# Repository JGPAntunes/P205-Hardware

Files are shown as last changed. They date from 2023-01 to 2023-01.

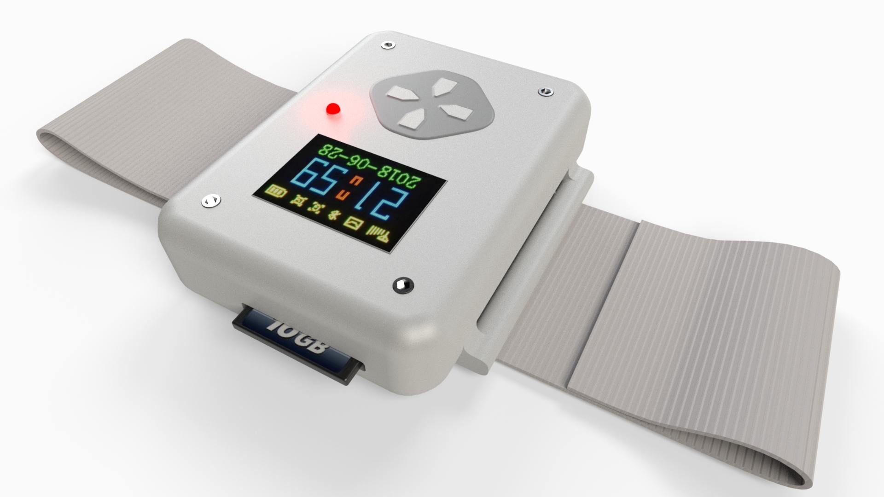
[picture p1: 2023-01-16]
Images/P205_Camera_Camera 2.jpg

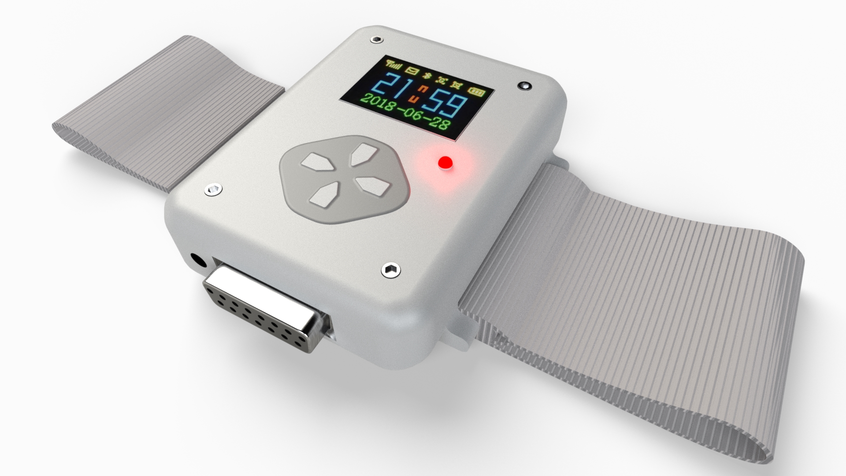
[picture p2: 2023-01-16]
Images/P205_Camera_Camera1.jpg

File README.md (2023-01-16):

# P205-Hardware
This repository was imported from GITLAB manualy, so no commits or branches are available.

This project aims to reliably obtain an ECG and all the signal metrics, and provide real-time alerts. 

These alerts would be sent to the medical staff, and through a graphical interface can confirm the patient ID, contact details and their location (GPS and/or cell triangulation). 

This does not change the fact that it is still a recording device, since the signals are recorded internally on an SD card 
This makes it possible for the data to be interpreted on a hospital environment, by the medical team.

PCB was designed from scratch for this usecase, the Signal Aquisition Medical Board (SAMB).

PCB Specifications:

	• Dual nRF52832 (one for data aquisition and one communications and overhaul system)

	• External RAM for MCU communication bridge

	• ADS1298 and ADS1296 for data aquisition

	• Precision NTC temperature sensing

	• SIM7080G for NB-IoT and GNSS 

	• SD card datalogging

	• BLE comunication (via the master nRF MCU)

	• USB battery charging (type C, no PD charging)

	• Wireless battery charging

	• DSUB-15 connector for eletrodes cable

	• 5mm jack for NTC sensor

	• ESD protection

	• Defibrillator discharge protection

	• OLED display (SPI)

	• Buzzer

	• Small external PCB with UI buttons

PCB Details:

	• Dimentions: 100mm x 95mm.

	• Soldermask: Black.

	• 4 layer IS400 18µm/35µm.

	• Tolerances:

	o OL-TT-TP-PP: 0.100mm (camadas exteriores)

	o OL‐TW: 0.125mm

	o OAR: 0.100mm

	o Via size 0.1mm drill

	o BGA pitch 0.8mm

	• Ni/Au.

	• Double side PCBA.

	• 4 M3 PTH.

	• Star-ground

	• 3 seperated ground planes (analog, digital e power).

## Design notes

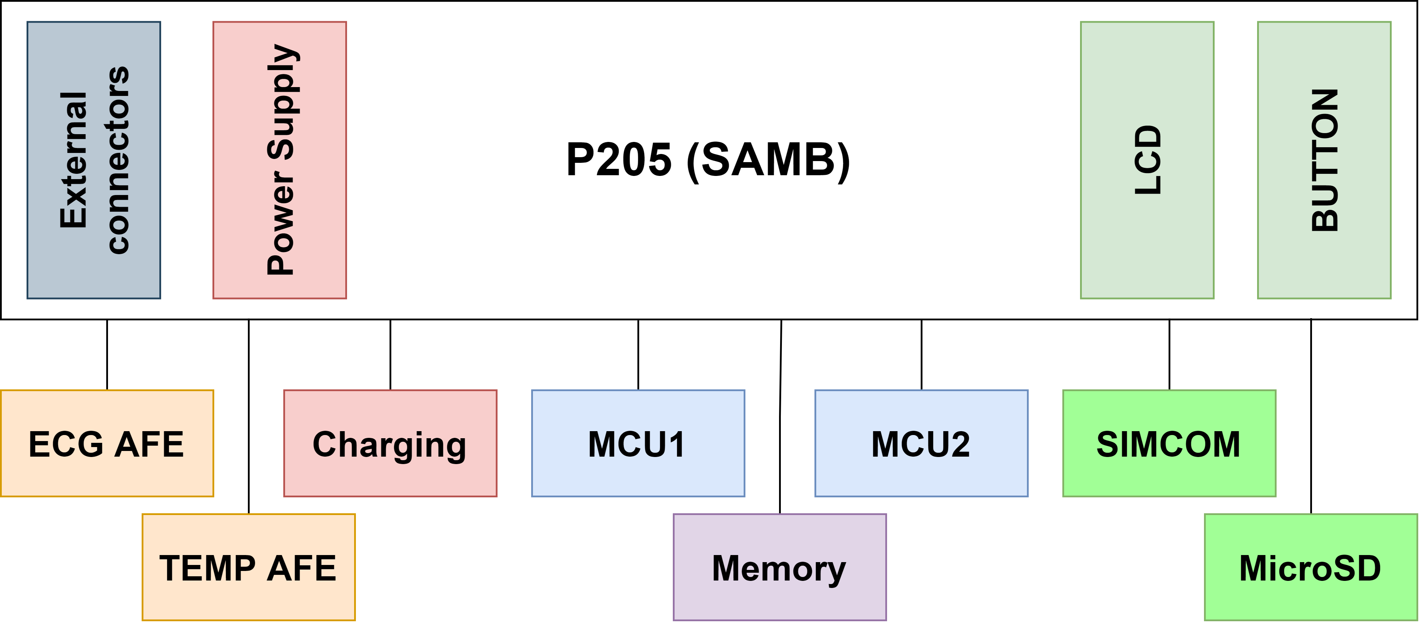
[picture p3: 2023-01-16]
Images/Diagrams/hardware_diagram.png

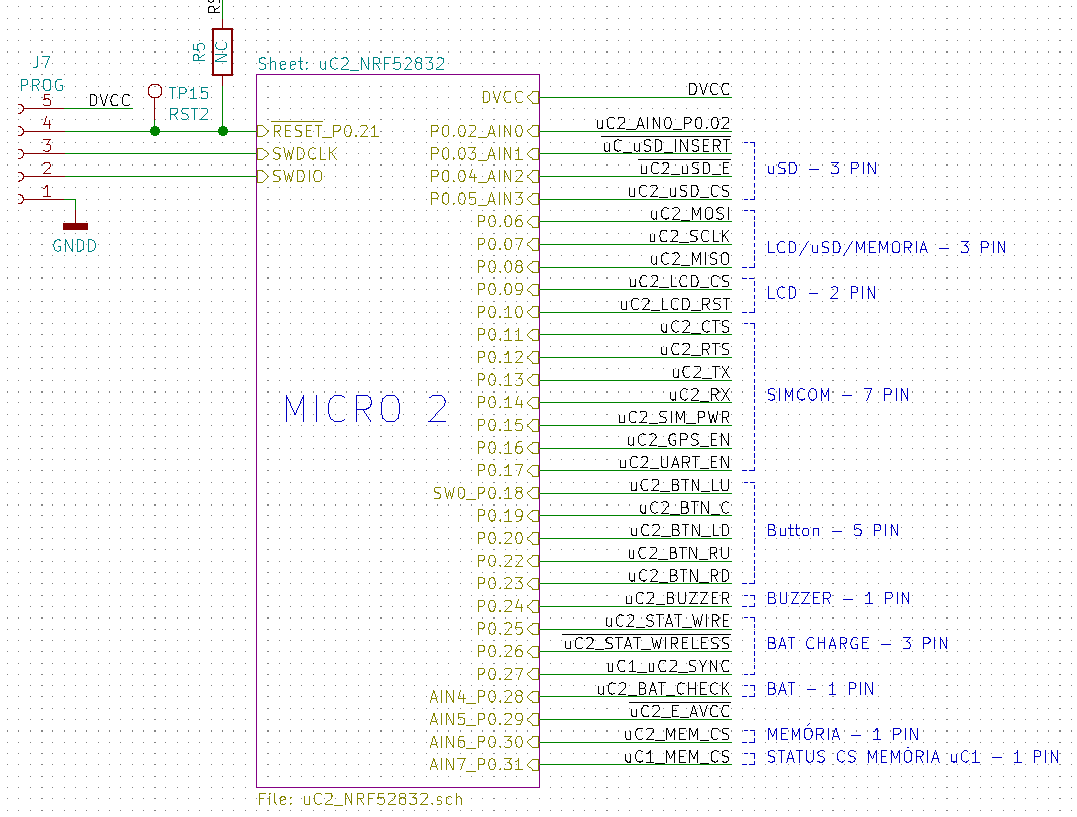
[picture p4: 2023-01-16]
Images/Diagrams/MCU2.png

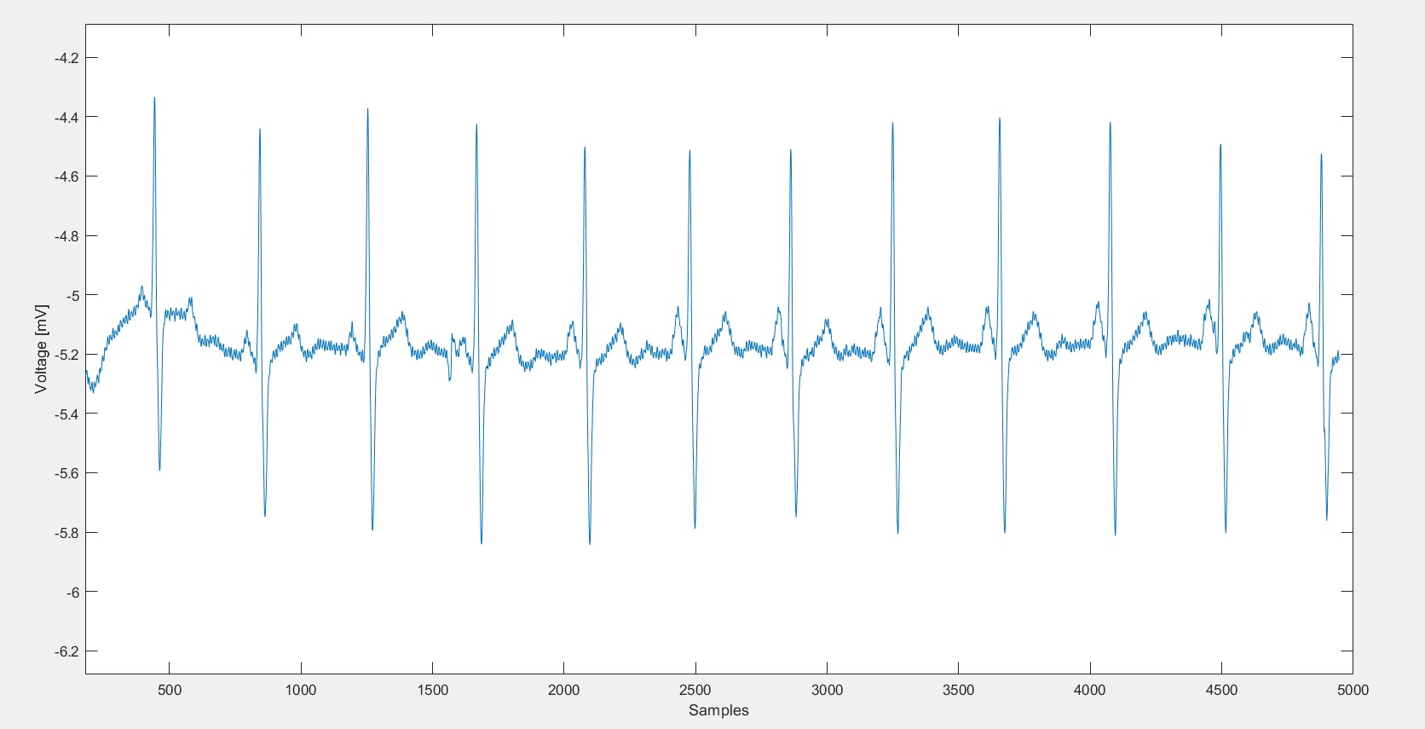
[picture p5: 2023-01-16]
Images/Sensors/filtered33.jpeg

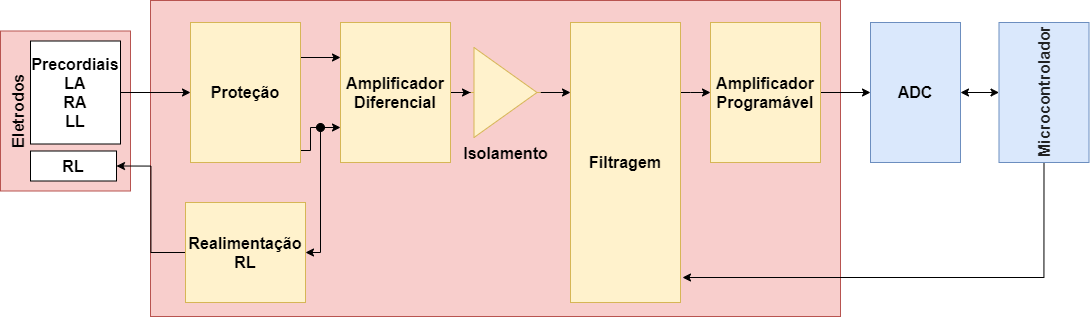
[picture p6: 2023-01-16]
Images/Diagrams/diagramas_sensoresv2.png

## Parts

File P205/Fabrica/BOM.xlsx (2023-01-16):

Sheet: BOM_All
# | References | Manufacturer_Part_Number | Description | Value | Manufacturer_Part_Number | Footprint | Qnt
1 | BZ1 | CSQG703BP | Buzzer, polarized | Buzzer | CSQG703BP | PinHeader_1x02_P1.27mm | 1
2 | C110 | CL05C120JB51PNC | Unpolarized capacitor | 12p | CL05C120JB51PNC | C_0402_1005Metric | 1
3 | C111 | CL05C120JB51PNC | Unpolarized capacitor | 12p | CL05C120JB51PNC | C_0402_1005Metric | 1
4 | C113 | CL05C120JB51PNC | Unpolarized capacitor | 12p | CL05C120JB51PNC | C_0402_1005Metric | 1
5 | C114 | CL05C120JB51PNC | Unpolarized capacitor | 12p | CL05C120JB51PNC | C_0402_1005Metric | 1
6 | C72 | CL05C120JB51PNC | Unpolarized capacitor | 12p | CL05C120JB51PNC | C_0402_1005Metric | 1
7 | C73 | CL05C120JB51PNC | Unpolarized capacitor | 12p | CL05C120JB51PNC | C_0402_1005Metric | 1
8 | C74 | CL05C120JB51PNC | Unpolarized capacitor | 12p | CL05C120JB51PNC | C_0402_1005Metric | 1
9 | C75 | CL05C120JB51PNC | Unpolarized capacitor | 12p | CL05C120JB51PNC | C_0402_1005Metric | 1
10 | C36 | C0402C103K5RAC7411 | Unpolarized capacitor | 22p | C0402C103K5RAC7411 | C_0402_1005Metric | 1
11 | C119 | CL05C221JB51PNC | Unpolarized capacitor | 220p | CL05C221JB51PNC | C_0402_1005Metric | 1
12 | C127 | CL05C221JB51PNC | Unpolarized capacitor | 220p | CL05C221JB51PNC | C_0402_1005Metric | 1
13 | C128 | CL05C221JB51PNC | Unpolarized capacitor | 220p | CL05C221JB51PNC | C_0402_1005Metric | 1
14 | C15 | CL05C221JB51PNC | Unpolarized capacitor | 220p | CL05C221JB51PNC | C_0402_1005Metric | 1
15 | C16 | CL05C221JB51PNC | Unpolarized capacitor | 220p | CL05C221JB51PNC | C_0402_1005Metric | 1
16 | C80 | CL05C221JB51PNC | Unpolarized capacitor | 220p | CL05C221JB51PNC | C_0402_1005Metric | 1
17 | C19 | 04025C102KAT4A | Unpolarized capacitor | 1n | 04025C102KAT4A | C_0402_1005Metric | 1
18 | C20 | 04025C102KAT4A | Unpolarized capacitor | 1n | 04025C102KAT4A | C_0402_1005Metric | 1
19 | C125 | C0402C103K5RAC7411 | Unpolarized capacitor | 10n | C0402C103K5RAC7411 | C_0402_1005Metric | 1
20 | C126 | C0402C103K5RAC7411 | Unpolarized capacitor | 10n | C0402C103K5RAC7411 | C_0402_1005Metric | 1
21 | C17 | C0402C103K5RAC7411 | Unpolarized capacitor | 10n | C0402C103K5RAC7411 | C_0402_1005Metric | 1
22 | C18 | C0402C103K5RAC7411 | Unpolarized capacitor | 10n | C0402C103K5RAC7411 | C_0402_1005Metric | 1
23 | C27 | C0402C103K5RAC7411 | Unpolarized capacitor | 10n | C0402C103K5RAC7411 | C_0402_1005Metric | 1
24 | C42 | C0402C103K5RAC7411 | Unpolarized capacitor | 10n | C0402C103K5RAC7411 | C_0402_1005Metric | 1
25 | C45 | C0402C103K5RAC7411 | Unpolarized capacitor | 10n | C0402C103K5RAC7411 | C_0402_1005Metric | 1
26 | C91 | C0402C103K5RAC7411 | Unpolarized capacitor | 10n | C0402C103K5RAC7411 | C_0402_1005Metric | 1
27 | C92 | C0402C103K5RAC7411 | Unpolarized capacitor | 10n | C0402C103K5RAC7411 | C_0402_1005Metric | 1
28 | C94 | C0402C103K5RAC7411 | Unpolarized capacitor | 10n | C0402C103K5RAC7411 | C_0402_1005Metric | 1
29 | C95 | C0402C103K5RAC7411 | Unpolarized capacitor | 10n | C0402C103K5RAC7411 | C_0402_1005Metric | 1
30 | C_TUNE2_1 | C0402C103K5RAC7411 | Unpolarized capacitor | 10n | C0402C103K5RAC7411 | C_0402_1005Metric | 1
31 | C_TUNE2_2 | C0402C103K5RAC7411 | Unpolarized capacitor | 10n | C0402C103K5RAC7411 | C_0402_1005Metric | 1
32 | C_TUNE2_3 | C0402C103K5RAC7411 | Unpolarized capacitor | 10n | C0402C103K5RAC7411 | C_0402_1005Metric | 1
33 | C1 | GCM155R71H104KE02D | Unpolarized capacitor | 100n | GCM155R71H104KE02D | C_0402_1005Metric | 1
34 | C101 | GCM155R71H104KE02D | Unpolarized capacitor | 100n | GCM155R71H104KE02D | C_0402_1005Metric | 1
35 | C103 | GCM155R71H104KE02D | Unpolarized capacitor | 100n | GCM155R71H104KE02D | C_0402_1005Metric | 1
36 | C105 | GCM155R71H104KE02D | Unpolarized capacitor | 100n | GCM155R71H104KE02D | C_0402_1005Metric | 1
37 | C116 | GCM155R71H104KE02D | Unpolarized capacitor | 100n | GCM155R71H104KE02D | C_0402_1005Metric | 1
38 | C117 | GCM155R71H104KE02D | Unpolarized capacitor | 100n | GCM155R71H104KE02D | C_0402_1005Metric | 1
39 | C121 | GCM155R71H104KE02D | Unpolarized capacitor | 100n | GCM155R71H104KE02D | C_0402_1005Metric | 1
40 | C124 | GCM155R71H104KE02D | Unpolarized capacitor | 100n | GCM155R71H104KE02D | C_0402_1005Metric | 1
41 | C23 | GCM155R71H104KE02D | Unpolarized capacitor | 100n | GCM155R71H104KE02D | C_0402_1005Metric | 1
42 | C24 | GCM155R71H104KE02D | Unpolarized capacitor | 100n | GCM155R71H104KE02D | C_0402_1005Metric | 1
43 | C30 | GCM155R71H104KE02D | Unpolarized capacitor | 100n | GCM155R71H104KE02D | C_0402_1005Metric | 1
44 | C31 | GCM155R71H104KE02D | Unpolarized capacitor | 100n | GCM155R71H104KE02D | C_0402_1005Metric | 1
45 | C32 | GCM155R71H104KE02D | Unpolarized capacitor | 100n | GCM155R71H104KE02D | C_0402_1005Metric | 1
46 | C4 | GCM155R71H104KE02D | Unpolarized capacitor | 100n | GCM155R71H104KE02D | C_0402_1005Metric | 1
47 | C40 | GCM155R71H104KE02D | Unpolarized capacitor | 100n | GCM155R71H104KE02D | C_0402_1005Metric | 1
48 | C41 | GCM155R71H104KE02D | Unpolarized capacitor | 100n | GCM155R71H104KE02D | C_0402_1005Metric | 1
49 | C43 | GCM155R71H104KE02D | Unpolarized capacitor | 100n | GCM155R71H104KE02D | C_0402_1005Metric | 1
50 | C44 | GCM155R71H104KE02D | Unpolarized capacitor | 100n | GCM155R71H104KE02D | C_0402_1005Metric | 1
51 | C48 | GCM155R71H104KE02D | Unpolarized capacitor | 100n | GCM155R71H104KE02D | C_0402_1005Metric | 1
52 | C49 | GCM155R71H104KE02D | Unpolarized capacitor | 100n | GCM155R71H104KE02D | C_0402_1005Metric | 1
53 | C5 | GCM155R71H104KE02D | Unpolarized capacitor | 100n | GCM155R71H104KE02D | C_0402_1005Metric | 1
54 | C50 | GCM155R71H104KE02D | Unpolarized capacitor | 100n | GCM155R71H104KE02D | C_0402_1005Metric | 1
55 | C51 | GCM155R71H104KE02D | Unpolarized capacitor | 100n | GCM155R71H104KE02D | C_0402_1005Metric | 1
56 | C52 | GCM155R71H104KE02D | Unpolarized capacitor | 100n | GCM155R71H104KE02D | C_0402_1005Metric | 1
57 | C58 | GCM155R71H104KE02D | Unpolarized capacitor | 100n | GCM155R71H104KE02D | C_0402_1005Metric | 1
58 | C59 | GCM155R71H104KE02D | Unpolarized capacitor | 100n | GCM155R71H104KE02D | C_0402_1005Metric | 1
59 | C60 | GCM155R71H104KE02D | Unpolarized capacitor | 100n | GCM155R71H104KE02D | C_0402_1005Metric | 1
60 | C64 | GCM155R71H104KE02D | Unpolarized capacitor | 100n | GCM155R71H104KE02D | C_0402_1005Metric | 1
61 | C67 | GCM155R71H104KE02D | Unpolarized capacitor | 100n | GCM155R71H104KE02D | C_0402_1005Metric | 1
62 | C68 | GCM155R71H104KE02D | Unpolarized capacitor | 100n | GCM155R71H104KE02D | C_0402_1005Metric | 1
63 | C71 | GCM155R71H104KE02D | Unpolarized capacitor | 100n | GCM155R71H104KE02D | C_0402_1005Metric | 1
64 | C77 | GCM155R71H104KE02D | Unpolarized capacitor | 100n | GCM155R71H104KE02D | C_0402_1005Metric | 1
65 | C78 | GCM155R71H104KE02D | Unpolarized capacitor | 100n | GCM155R71H104KE02D | C_0402_1005Metric | 1
66 | C82 | GCM155R71H104KE02D | Unpolarized capacitor | 100n | GCM155R71H104KE02D | C_0402_1005Metric | 1
67 | C84 | GCM155R71H104KE02D | Unpolarized capacitor | 100n | GCM155R71H104KE02D | C_0402_1005Metric | 1
68 | C89 | C1005X5R1E474K050BB | Unpolarized capacitor | 0.47u | C1005X5R1E474K050BB | C_0402_1005Metric | 1
69 | C90 | C1005X5R1E474K050BB | Unpolarized capacitor | 0.47u | C1005X5R1E474K050BB | C_0402_1005Metric | 1
70 | C_TUNE1_3 | C1005X5R1E474K050BB | Unpolarized capacitor | 0.47u | C1005X5R1E474K050BB | C_0402_1005Metric | 1
71 | C100 | GRT155R61E105KE01D | Unpolarized capacitor | 1u | GRT155R61E105KE01D | C_0402_1005Metric | 1
72 | C102 | GRT155R61E105KE01D | Unpolarized capacitor | 1u | GRT155R61E105KE01D | C_0402_1005Metric | 1
73 | C118 | GRT155R61E105KE01D | Unpolarized capacitor | 1u | GRT155R61E105KE01D | C_0402_1005Metric | 1
74 | C129 | GRT155R61E105KE01D | Unpolarized capacitor | 1u | GRT155R61E105KE01D | C_0402_1005Metric | 1
75 | C130 | GRT155R61E105KE01D | Unpolarized capacitor | 1u | GRT155R61E105KE01D | C_0402_1005Metric | 1
76 | C25 | GRT155R61E105KE01D | Unpolarized capacitor | 1u | GRT155R61E105KE01D | C_0402_1005Metric | 1
77 | C26 | GRT155R61E105KE01D | Unpolarized capacitor | 1u | GRT155R61E105KE01D | C_0402_1005Metric | 1
78 | C28 | GRT155R61E105KE01D | Unpolarized capacitor | 1u | GRT155R61E105KE01D | C_0402_1005Metric | 1
79 | C29 | GRT155R61E105KE01D | Unpolarized capacitor | 1u | GRT155R61E105KE01D | C_0402_1005Metric | 1
80 | C33 | GRT155R61E105KE01D | Unpolarized capacitor | 1u | GRT155R61E105KE01D | C_0402_1005Metric | 1
81 | C34 | GRT155R61E105KE01D | Unpolarized capacitor | 1u | GRT155R61E105KE01D | C_0402_1005Metric | 1
82 | C46 | GRT155R61E105KE01D | Unpolarized capacitor | 1u | GRT155R61E105KE01D | C_0402_1005Metric | 1
83 | C47 | GRT155R61E105KE01D | Unpolarized capacitor | 1u | GRT155R61E105KE01D | C_0402_1005Metric | 1
84 | C54 | GRT155R61E105KE01D | Unpolarized capacitor | 1u | GRT155R61E105KE01D | C_0402_1005Metric | 1
85 | C55 | GRT155R61E105KE01D | Unpolarized capacitor | 1u | GRT155R61E105KE01D | C_0402_1005Metric | 1
86 | C56 | GRT155R61E105KE01D | Unpolarized capacitor | 1u | GRT155R61E105KE01D | C_0402_1005Metric | 1
87 | C62 | GRT155R61E105KE01D | Unpolarized capacitor | 1u | GRT155R61E105KE01D | C_0402_1005Metric | 1
88 | C79 | GRT155R61E105KE01D | Unpolarized capacitor | 1u | GRT155R61E105KE01D | C_0402_1005Metric | 1
89 | C83 | GRT155R61E105KE01D | Unpolarized capacitor | 1u | GRT155R61E105KE01D | C_0402_1005Metric | 1
90 | C93 | GRT155R61E105KE01D | Unpolarized capacitor | 1u | GRT155R61E105KE01D | C_0402_1005Metric | 1
91 | C96 | GRT155R61E105KE01D | Unpolarized capacitor | 1u | GRT155R61E105KE01D | C_0402_1005Metric | 1
92 | C_TUNE1_1 | GRT155R61E105KE01D | Unpolarized capacitor | 1u | GRT155R61E105KE01D | C_0402_1005Metric | 1
93 | C_TUNE1_2 | GRT155R61E105KE01D | Unpolarized capacitor | 1u | GRT155R61E105KE01D | C_0402_1005Metric | 1
94 | C115 | CL21A475KLCLQNC | Unpolarized capacitor | 4.7u | CL21A475KLCLQNC | C_0805_2012Metric | 1
95 | C123 | CL21A475KLCLQNC | Unpolarized capacitor | 4.7u | CL21A475KLCLQNC | C_0805_2012Metric | 1
96 | C76 | CL21A475KLCLQNC | Unpolarized capacitor | 4.7u | CL21A475KLCLQNC | C_0805_2012Metric | 1
97 | C106 | TMK212BBJ106MG-T | Unpolarized capacitor | 10u | TMK212BBJ106MG-T | C_0805_2012Metric | 1
98 | C131 | TMK212BBJ106MG-T | Unpolarized capacitor | 10u | TMK212BBJ106MG-T | C_0805_2012Metric | 1
99 | C21 | TMK212BBJ106MG-T | Unpolarized capacitor | 10u | TMK212BBJ106MG-T | C_0805_2012Metric | 1
100 | C22 | TMK212BBJ106MG-T | Unpolarized capacitor | 10u | TMK212BBJ106MG-T | C_0805_2012Metric | 1
101 | C35 | TMK212BBJ106MG-T | Unpolarized capacitor | 10u | TMK212BBJ106MG-T | C_0805_2012Metric | 1
102 | C37 | TMK212BBJ106MG-T | Unpolarized capacitor | 10u | TMK212BBJ106MG-T | C_0805_2012Metric | 1
103 | C38 | TMK212BBJ106MG-T | Unpolarized capacitor | 10u | TMK212BBJ106MG-T | C_0805_2012Metric | 1
104 | C39 | TMK212BBJ106MG-T | Unpolarized capacitor | 10u | TMK212BBJ106MG-T | C_0805_2012Metric | 1
105 | C53 | TMK212BBJ106MG-T | Unpolarized capacitor | 10u | TMK212BBJ106MG-T | C_0805_2012Metric | 1
106 | C57 | TMK212BBJ106MG-T | Unpolarized capacitor | 10u | TMK212BBJ106MG-T | C_0805_2012Metric | 1
107 | C69 | TMK212BBJ106MG-T | Unpolarized capacitor | 10u | TMK212BBJ106MG-T | C_0805_2012Metric | 1
108 | C70 | TMK212BBJ106MG-T | Unpolarized capacitor | 10u | TMK212BBJ106MG-T | C_0805_2012Metric | 1
109 | C97 | TMK212BBJ106MG-T | Unpolarized capacitor | 10u | TMK212BBJ106MG-T | C_0805_2012Metric | 1
110 | C98 | TMK212BBJ106MG-T | Unpolarized capacitor | 10u | TMK212BBJ106MG-T | C_0805_2012Metric | 1
111 | C99 | TMK212BBJ106MG-T | Unpolarized capacitor | 10u | TMK212BBJ106MG-T | C_0805_2012Metric | 1
112 | C85 | TAJB107K006TNJ | Polarized capacitor, US symbol | 100u | TAJB107K006TNJ | C_1210_3225Metric | 1
113 | C86 | TAJB107K006TNJ | Polarized capacitor, US symbol | 100u | TAJB107K006TNJ | C_1210_3225Metric | 1
114 | C87 | TAJB107K006TNJ | Polarized capacitor, US symbol | 100u | TAJB107K006TNJ | C_1210_3225Metric | 1
115 | C10 |  | Unpolarized capacitor | NC |  |  | 1
116 | C104 |  | Unpolarized capacitor | NC |  |  | 1
117 | C107 |  | Unpolarized capacitor | NC |  |  | 1
118 | C108 |  | Unpolarized capacitor | NC |  |  | 1
119 | C109 |  | Unpolarized capacitor | NC |  |  | 1
120 | C11 |  | Unpolarized capacitor | NC |  |  | 1
121 | C112 |  | Unpolarized capacitor | NC |  |  | 1
122 | C12 |  | Unpolarized capacitor | NC |  |  | 1
123 | C120 |  | Unpolarized capacitor | NC |  |  | 1
124 | C122 |  | Unpolarized capacitor | NC |  |  | 1
125 | C13 |  | Unpolarized capacitor | NC |  |  | 1
126 | C14 |  | Unpolarized capacitor | NC |  |  | 1
127 | C6 |  | Unpolarized capacitor | NC |  |  | 1
128 | C7 |  | Unpolarized capacitor | NC |  |  | 1
129 | C8 |  | Unpolarized capacitor | NC |  |  | 1
130 | C81 |  | Unpolarized capacitor | NC |  |  | 1
131 | C9 |  | Unpolarized capacitor | NC |  |  | 1
132 | C2 |  | Unpolarized capacitor | TUNE |  | C_0402_1005Metric | 1
133 | C3 |  | Unpolarized capacitor | TUNE |  | C_0402_1005Metric | 1
134 | C88 |  | Unpolarized capacitor | TUNE |  | C_0402_1005Metric | 1
135 | D32 | APHBM2012LVBDZGKC | Dual LED, cathodes on pins 2 and 4 | APHBM2012LVBDZGKC | APHBM2012LVBDZGKC | LED_2C | 1
136 | D1 | DESD5V0U1BA-7 | Bidirectional transient-voltage-suppression diode | DESD5V0U1BA-7 | DESD5V0U1BA-7 | D_SOD-323 | 1
137 | D10 | DESD5V0U1BA-7 | Bidirectional transient-voltage-suppression diode | DESD5V0U1BA-7 | DESD5V0U1BA-7 | D_SOD-323 | 1
138 | D11 | DESD5V0U1BA-7 | Bidirectional transient-voltage-suppression diode | DESD5V0U1BA-7 | DESD5V0U1BA-7 | D_SOD-323 | 1
139 | D12 | DESD5V0U1BA-7 | Bidirectional transient-voltage-suppression diode | DESD5V0U1BA-7 | DESD5V0U1BA-7 | D_SOD-323 | 1
140 | D13 | DESD5V0U1BA-7 | Bidirectional transient-voltage-suppression diode | DESD5V0U1BA-7 | DESD5V0U1BA-7 | D_SOD-323 | 1
141 | D16 | DESD5V0U1BA-7 | Bidirectional transient-voltage-suppression diode | DESD5V0U1BA-7 | DESD5V0U1BA-7 | D_SOD-323 | 1
142 | D17 | DESD5V0U1BA-7 | Bidirectional transient-voltage-suppression diode | DESD5V0U1BA-7 | DESD5V0U1BA-7 | D_SOD-323 | 1
143 | D18 | DESD5V0U1BA-7 | Bidirectional transient-voltage-suppression diode | DESD5V0U1BA-7 | DESD5V0U1BA-7 | D_SOD-323 | 1
144 | D19 | DESD5V0U1BA-7 | Bidirectional transient-voltage-suppression diode | DESD5V0U1BA-7 | DESD5V0U1BA-7 | D_SOD-323 | 1
145 | D2 | DESD5V0U1BA-7 | Bidirectional transient-voltage-suppression diode | DESD5V0U1BA-7 | DESD5V0U1BA-7 | D_SOD-323 | 1
146 | D20 | DESD5V0U1BA-7 | Bidirectional transient-voltage-suppression diode | DESD5V0U1BA-7 | DESD5V0U1BA-7 | D_SOD-323 | 1
147 | D21 | DESD5V0U1BA-7 | Bidirectional transient-voltage-suppression diode | DESD5V0U1BA-7 | DESD5V0U1BA-7 | D_SOD-323 | 1
148 | D22 | DESD5V0U1BA-7 | Bidirectional transient-voltage-suppression diode | DESD5V0U1BA-7 | DESD5V0U1BA-7 | D_SOD-323 | 1
149 | D23 | DESD5V0U1BA-7 | Bidirectional transient-voltage-suppression diode | DESD5V0U1BA-7 | DESD5V0U1BA-7 | D_SOD-323 | 1
150 | D24 | DESD5V0U1BA-7 | Bidirectional transient-voltage-suppression diode | DESD5V0U1BA-7 | DESD5V0U1BA-7 | D_SOD-323 | 1
151 | D25 | DESD5V0U1BA-7 | Bidirectional transient-voltage-suppression diode | DESD5V0U1BA-7 | DESD5V0U1BA-7 | D_SOD-323 | 1
152 | D26 | DESD5V0U1BA-7 | Bidirectional transient-voltage-suppression diode | DESD5V0U1BA-7 | DESD5V0U1BA-7 | D_SOD-323 | 1
153 | D27 | DESD5V0U1BA-7 | Bidirectional transient-voltage-suppression diode | DESD5V0U1BA-7 | DESD5V0U1BA-7 | D_SOD-323 | 1
154 | D28 | DESD5V0U1BA-7 | Bidirectional transient-voltage-suppression diode | DESD5V0U1BA-7 | DESD5V0U1BA-7 | D_SOD-323 | 1
155 | D29 | DESD5V0U1BA-7 | Bidirectional transient-voltage-suppression diode | DESD5V0U1BA-7 | DESD5V0U1BA-7 | D_SOD-323 | 1
156 | D3 | DESD5V0U1BA-7 | Bidirectional transient-voltage-suppression diode | DESD5V0U1BA-7 | DESD5V0U1BA-7 | D_SOD-323 | 1
157 | D4 | DESD5V0U1BA-7 | Bidirectional transient-voltage-suppression diode | DESD5V0U1BA-7 | DESD5V0U1BA-7 | D_SOD-323 | 1
158 | D5 | DESD5V0U1BA-7 | Bidirectional transient-voltage-suppression diode | DESD5V0U1BA-7 | DESD5V0U1BA-7 | D_SOD-323 | 1
159 | D6 | DESD5V0U1BA-7 | Bidirectional transient-voltage-suppression diode | DESD5V0U1BA-7 | DESD5V0U1BA-7 | D_SOD-323 | 1
160 | D7 | DESD5V0U1BA-7 | Bidirectional transient-voltage-suppression diode | DESD5V0U1BA-7 | DESD5V0U1BA-7 | D_SOD-323 | 1
161 | D8 | DESD5V0U1BA-7 | Bidirectional transient-voltage-suppression diode | DESD5V0U1BA-7 | DESD5V0U1BA-7 | D_SOD-323 | 1
162 | D9 | DESD5V0U1BA-7 | Bidirectional transient-voltage-suppression diode | DESD5V0U1BA-7 | DESD5V0U1BA-7 | D_SOD-323 | 1
163 | D14 | FML340A-W | Schottky diode | FML340A-W | FML340A-W | D_SMA | 1
164 | D15 | FML340A-W | Schottky diode | FML340A-W | FML340A-W | D_SMA | 1
165 | D30 | FML340A-W | Schottky diode | FML340A-W | FML340A-W | D_SMA | 1
166 | D31 | FML340A-W | Schottky diode | FML340A-W | FML340A-W | D_SMA | 1
167 | D33 | FML340A-W | Schottky diode | FML340A-W | FML340A-W | D_SMA | 1
168 | D34 | FML340A-W | Schottky diode | FML340A-W | FML340A-W | D_SMA | 1
169 | FB1 | BLM21SP601SH1D | Ferrite bead | BLM21SP601SH1D | BLM21SP601SH1D | R_0805_2012Metric | 1
170 | FB2 | BLM21SP601SH1D | Ferrite bead | BLM21SP601SH1D | BLM21SP601SH1D | R_0805_2012Metric | 1
171 | IC6 | 23K640-I/ST | Microchip Technology SRAM, 23K640-I/ST- 64kbit | 23K640-I_ST | 23K640-I/ST | SOP65P640X120-8N | 1
172 | IC1 | ADS1296RIZXGT | 6-Channel, 24-Bit Analog-To-Digital Converter w/Integrated Respiration | ADS1296RIZXGT | ADS1296RIZXGT | BGA64C80P8X8_800X800X145 | 1
173 | IC2 | ADS1298IPAG | 8-Channel 24-bit ADC With Integrated ECG Front End | ADS1298IPAG | ADS1298IPAG | QFP50P1200X1200X120-64N | 1
174 | IC3 | BQ51050BRHLR | Qi (WPC) Compliant Highly Integrated Secondary-Side Direct Lithium Ion Charger. | BQ51050BRHLR | BQ51050BRHLR | BQ51050BRHLR | 1
175 | IC4 | SN74HCS00QPWRQ1 | Logic Gates | SN74HCS00QPWRQ1 | SN74HCS00QPWRQ1 | SOP65P640X120-14N | 1
176 | J14 | 12401598E4#2A |  | 12401598E4#2A | 12401598E4#2A | AMPHENOL_12401598E4#2A | 1
177 | J3 | WS |  | 70-IWAS4532AGB140KF1 | WS | PinSocket_1x02_P2.54mm_Vertical | 1
178 | J2 | M40-4010446 |  | Batt | M40-4010446 | M404010446 | 1
179 | J8 | WS | Generic connector, single row, 01x14, | EXP1 | WS | PinSocket_2x08_P1.27mm_Horizontal | 1
180 | J16 | WS | Generic connector, single row, 01x14, | EXP2 | WS | PinSocket_2x08_P1.27mm_Horizontal | 1
181 | J1 | MEM2061-01-188-00-A | MEM2061 Series 8 Position 1.1 mm Pitch Push-Push MicroSD SMT Memory Card Connector | MEM2061-01-188-00-A | MEM2061-01-188-00-A | MEM20610118800A | 1
182 | J5 | WS | Audio Jack, 2 Poles (Mono / TS), Grounded Sleeve, Switched T Pole (Normalling) | NTC Connector | WS | M404010246 | 1
183 | J6 | WS | Generic connector, single row, 01x05 | PROG | WS | PinSocket_1x05_P2.54mm_Vertical | 1
184 | J7 | WS | Generic connector, single row, 01x05 | PROG | WS | PinSocket_1x05_P2.54mm_Vertical | 1
185 | J10 | SIM8051-6-0-14-00-A | SIM Card | SIM_Card | SIM8051-6-0-14-00-A | SIM8051601401A | 1
186 | J12 | U.FL-R-SMT-1(10) |  | U.FL-R-SMT-1(10) | U.FL-R-SMT-1(10) | CONUFL001-SMD | 1
187 | J13 | U.FL-R-SMT-1(10) |  | U.FL-R-SMT-1(10) | U.FL-R-SMT-1(10) | CONUFL001-SMD | 1
188 | J15 | U.FL-R-SMT-1(10) |  | U.FL-R-SMT-1(10) | U.FL-R-SMT-1(10) | CONUFL001-SMD | 1
189 | J11 | WS | Generic connector, double row, 02x03 | USB/BATT | WS | PinHeader_2x03_P2.54mm_Vertical | 1
190 | J17 | WS | Generic connector, double row, 02x03 | USB/BATT | WS | PinHeader_2x03_P2.54mm_Vertical | 1
191 | L2 | 7447840115 | Inductor | 15n | 7447840115 | L_0402_1005Metric | 1
192 | L8 | 7447840115 | Inductor | 15n | 7447840115 | L_0402_1005Metric | 1
193 | L6 | TYA2520121R0M-10 | Inductor | 1uH | TYA2520121R0M-10 | L_1008_2520Metric | 1
194 | L1 | MLZ1608M100WTD25 | Inductor | 10u | MLZ1608M100WTD25 | L_0603_1608Metric | 1
195 | L9 | MLZ1608M100WTD25 | Inductor | 10u | MLZ1608M100WTD25 | L_0603_1608Metric | 1
196 | L7 |  | Inductor symbol for simulation only | NC |  |  | 1
197 | L3 |  | Inductor | TUNE |  | C_0402_1005Metric | 1
198 | L4 |  | Inductor | TUNE |  | C_0402_1005Metric | 1
199 | L5 |  | Inductor | TUNE |  | C_0402_1005Metric | 1
200 | NT1 |  | Net tie, 3 pins, tee | STAR GROUND |  | NINJA_STAR_GROUND | 1
201 | Q1 | DMG2305UX-7 | MOSFET P-Ch 20V 5A Enhancement SOT23 Diodes | DMG2305 | DMG2305UX-7 | SOT-23 | 1
202 | Q3 | DMG2305UX-7 | MOSFET P-Ch 20V 5A Enhancement SOT23 Diodes | DMG2305 | DMG2305UX-7 | SOT-23 | 1
203 | Q4 | DMG2305UX-7 | MOSFET P-Ch 20V 5A Enhancement SOT23 Diodes | DMG2305 | DMG2305UX-7 | SOT-23 | 1
204 | Q2 | PMV15ENEAR | N-MOSFET transistor, gate/source/drain | PMV15ENEAR | PMV15ENEAR | SOT-23 | 1
205 | R36 | SFR01MZPJ000 | Resistor | 0 | SFR01MZPJ000 | R_0402_1005Metric | 1
206 | R39 | SFR01MZPJ000 | Resistor | 0 | SFR01MZPJ000 | R_0402_1005Metric | 1
207 | R42 | SFR01MZPJ000 | Resistor | 0 | SFR01MZPJ000 | R_0402_1005Metric | 1
208 | R43 | SFR01MZPJ000 | Resistor | 0 | SFR01MZPJ000 | R_0402_1005Metric | 1
209 | R53 | SFR01MZPJ000 | Resistor | 0 | SFR01MZPJ000 | R_0402_1005Metric | 1
210 | R54 | SFR01MZPJ000 | Resistor | 0 | SFR01MZPJ000 | R_0402_1005Metric | 1
211 | R55 | SFR01MZPJ000 | Resistor | 0 | SFR01MZPJ000 | R_0402_1005Metric | 1
212 | R56 | SFR01MZPJ000 | Resistor | 0 | SFR01MZPJ000 | R_0402_1005Metric | 1
213 | R88 | CRCW06030000Z0EAC | Resistor | 0 | CRCW06030000Z0EAC | R_0603_1608Metric | 1
214 | R63 | CRCW0402330RJNEDHP | Resistor | 200 | CRCW0402330RJNEDHP | R_0402_1005Metric | 1
215 | R77 | Resistor_SMD:R_0402_1005Metric | Resistor | 200 | Resistor_SMD:R_0402_1005Metric | R_0402_1005Metric | 1
216 | R75 | CRCW0402270RFKEDHP | Resistor | 270 | CRCW0402270RFKEDHP | R_0402_1005Metric | 1
217 | R103 | CRCW0402330RJNEDHP | Resistor | 330 | CRCW0402330RJNEDHP | R_0402_1005Metric | 1
218 | R104 | CRCW0402330RJNEDHP | Resistor | 330 | CRCW0402330RJNEDHP | R_0402_1005Metric | 1
219 | R44 | CRCW0402330RJNEDHP | Resistor | 330 | CRCW0402330RJNEDHP | R_0402_1005Metric | 1
220 | R45 | CRCW0402330RJNEDHP | Resistor | 330 | CRCW0402330RJNEDHP | R_0402_1005Metric | 1
221 | R64 | CRCW0402330RJNEDHP | Resistor | 330 | CRCW0402330RJNEDHP | R_0402_1005Metric | 1
222 | R65 | CRCW0402330RJNEDHP | Resistor | 330 | CRCW0402330RJNEDHP | R_0402_1005Metric | 1
223 | R68 | CRCW0402330RJNEDHP | Resistor | 330 | CRCW0402330RJNEDHP | R_0402_1005Metric | 1
224 | R86 | CRCW0402330RJNEDHP | Resistor | 330 | CRCW0402330RJNEDHP | R_0402_1005Metric | 1
225 | R57 | RG1005N-3161-W-T1 | Resistor | 3.24k | RG1005N-3161-W-T1 | R_0402_1005Metric | 1
226 | R1 | SG73P1ETTP512J | Resistor | 5.1k | SG73P1ETTP512J | R_0402_1005Metric | 1
227 | R10 | SG73P1ETTP512J | Resistor | 5.1k | SG73P1ETTP512J | R_0402_1005Metric | 1
228 | R11 | SG73P1ETTP512J | Resistor | 5.1k | SG73P1ETTP512J | R_0402_1005Metric | 1
229 | R12 | SG73P1ETTP512J | Resistor | 5.1k | SG73P1ETTP512J | R_0402_1005Metric | 1
230 | R13 | SG73P1ETTP512J | Resistor | 5.1k | SG73P1ETTP512J | R_0402_1005Metric | 1
231 | R2 | SG73P1ETTP512J | Resistor | 5.1k | SG73P1ETTP512J | R_0402_1005Metric | 1
232 | R37 | SG73P1ETTP512J | Resistor | 5.1k | SG73P1ETTP512J | R_0402_1005Metric | 1
233 | R38 | SG73P1ETTP512J | Resistor | 5.1k | SG73P1ETTP512J | R_0402_1005Metric | 1
234 | R40 | SG73P1ETTP512J | Resistor | 5.1k | SG73P1ETTP512J | R_0402_1005Metric | 1
235 | R58 | SG73P1ETTP512J | Resistor | 5.1k | SG73P1ETTP512J | R_0402_1005Metric | 1
236 | R74 | SG73P1ETTP512J | Resistor | 5.1k | SG73P1ETTP512J | R_0402_1005Metric | 1
237 | R101 | RC0402JR-7W10KL | Resistor | 10k | RC0402JR-7W10KL | R_0402_1005Metric | 1
238 | R102 | RC0402JR-7W10KL | Resistor | 10k | RC0402JR-7W10KL | R_0402_1005Metric | 1
239 | R105 | RC0402JR-7W10KL | Resistor | 10k | RC0402JR-7W10KL | R_0402_1005Metric | 1
240 | R24 | MOS3CT631R103J | Resistor | 10k | MOS3CT631R103J | R_Axial_DIN0617_L17.0mm_D6.0mm | 1
241 | R25 | MOS3CT631R103J | Resistor | 10k | MOS3CT631R103J | R_Axial_DIN0617_L17.0mm_D6.0mm | 1
242 | R31 | RC0402JR-7W10KL | Resistor | 10k | RC0402JR-7W10KL | R_0402_1005Metric | 1
243 | R32 | RC0402JR-7W10KL | Resistor | 10k | RC0402JR-7W10KL | R_0402_1005Metric | 1
244 | R34 | RC0402JR-7W10KL | Resistor | 10k | RC0402JR-7W10KL | R_0402_1005Metric | 1
245 | R41 | RC0402JR-7W10KL | Resistor | 10k | RC0402JR-7W10KL | R_0402_1005Metric | 1
246 | R59 | RC0402JR-7W10KL | Resistor | 10k | RC0402JR-7W10KL | R_0402_1005Metric | 1
247 | R60 | RC0402JR-7W10KL | Resistor | 10k | RC0402JR-7W10KL | R_0402_1005Metric | 1
248 | R61 | CRCW0402100KFKEDC | Resistor | 10k | CRCW0402100KFKEDC | R_0402_1005Metric | 1
249 | R62 | CRCW0402100KFKEDC | Resistor | 10k | CRCW0402100KFKEDC | R_0402_1005Metric | 1
250 | R72 | RC0402JR-7W10KL | Resistor | 10k | RC0402JR-7W10KL | R_0402_1005Metric | 1
251 | R78 | RC0402JR-7W10KL | Resistor | 10k | RC0402JR-7W10KL | R_0402_1005Metric | 1
252 | R80 | RC0402JR-7W10KL | Resistor | 10k | RC0402JR-7W10KL | R_0402_1005Metric | 1
253 | R82 | RC0402JR-7W10KL | Resistor | 10k | RC0402JR-7W10KL | R_0402_1005Metric | 1
254 | R97 | RC0402JR-7W10KL | Resistor | 10k | RC0402JR-7W10KL | R_0402_1005Metric | 1
255 | R98 | RC0402JR-7W10KL | Resistor | 10k | RC0402JR-7W10KL | R_0402_1005Metric | 1
256 | R76 | ERJ-2RKF4222X | Resistor | 42.2k | ERJ-2RKF4222X | R_0402_1005Metric | 1
257 | R3 | 667-ERJ-2RKF7152X | Resistor | 71.5k | 667-ERJ-2RKF7152X | R_0402_1005Metric | 1
258 | R48 | 667-ERJ-2RKF7152X | Resistor | 71.5k | 667-ERJ-2RKF7152X | R_0402_1005Metric | 1
259 | R100 | CRCW0402100KFKEDC | Resistor | 100k | CRCW0402100KFKEDC | R_0402_1005Metric | 1
260 | R14 | RSF3WSJT-73-100K | Resistor | 100k | RSF3WSJT-73-100K | R_Axial_DIN0516_L15.5mm_D5.0mm | 1
261 | R15 | RSF3WSJT-73-100K | Resistor | 100k | RSF3WSJT-73-100K | R_Axial_DIN0516_L15.5mm_D5.0mm | 1
262 | R16 | RSF3WSJT-73-100K | Resistor | 100k | RSF3WSJT-73-100K | R_Axial_DIN0516_L15.5mm_D5.0mm | 1
263 | R17 | RSF3WSJT-73-100K | Resistor | 100k | RSF3WSJT-73-100K | R_Axial_DIN0516_L15.5mm_D5.0mm | 1
264 | R18 | RSF3WSJT-73-100K | Resistor | 100k | RSF3WSJT-73-100K | R_Axial_DIN0516_L15.5mm_D5.0mm | 1
265 | R19 | RSF3WSJT-73-100K | Resistor | 100k | RSF3WSJT-73-100K | R_Axial_DIN0516_L15.5mm_D5.0mm | 1
266 | R20 | RSF3WSJT-73-100K | Resistor | 100k | RSF3WSJT-73-100K | R_Axial_DIN0516_L15.5mm_D5.0mm | 1
267 | R21 | RSF3WSJT-73-100K | Resistor | 100k | RSF3WSJT-73-100K | R_Axial_DIN0516_L15.5mm_D5.0mm | 1
268 | R22 | RSF3WSJT-73-100K | Resistor | 100k | RSF3WSJT-73-100K | R_Axial_DIN0516_L15.5mm_D5.0mm | 1
269 | R23 | RSF3WSJT-73-100K | Resistor | 100k | RSF3WSJT-73-100K | R_Axial_DIN0516_L15.5mm_D5.0mm | 1
270 | R4 | CRCW0402100KFKEDC | Resistor | 100k | CRCW0402100KFKEDC | R_0402_1005Metric | 1
271 | R26 | RCS04021M00FKED | Resistor | 1M | RCS04021M00FKED | R_0402_1005Metric | 1
272 | R27 | RCS04021M00FKED | Resistor | 1M | RCS04021M00FKED | R_0402_1005Metric | 1
273 | R28 | RCS04021M00FKED | Resistor | 1M | RCS04021M00FKED | R_0402_1005Metric | 1
274 | R29 | RCS04021M00FKED | Resistor | 1M | RCS04021M00FKED | R_0402_1005Metric | 1
275 | R30 | RCS04021M00FKED | Resistor | 1M | RCS04021M00FKED | R_0402_1005Metric | 1
276 | R33 | RCS04021M00FKED | Resistor | 1M | RCS04021M00FKED | R_0402_1005Metric | 1
277 | R35 | RCS04021M00FKED | Resistor | 1M | RCS04021M00FKED | R_0402_1005Metric | 1
278 | R46 | RCS04021M00FKED | Resistor | 1M | RCS04021M00FKED | R_0402_1005Metric | 1
279 | R47 | RCS04021M00FKED | Resistor | 1M | RCS04021M00FKED | R_0402_1005Metric | 1
280 | R6 | RCS04021M00FKED | Resistor | 1M | RCS04021M00FKED | R_0402_1005Metric | 1
281 | R7 | RCS04021M00FKED | Resistor | 1M | RCS04021M00FKED | R_0402_1005Metric | 1
282 | R8 | RCS04021M00FKED | Resistor | 1M | RCS04021M00FKED | R_0402_1005Metric | 1
283 | R9 | RCS04021M00FKED | Resistor | 1M | RCS04021M00FKED | R_0402_1005Metric | 1
284 | R51 | CRCW04021M13FKED | Resistor | 1.13M | CRCW04021M13FKED | R_0402_1005Metric | 1
285 | R52 | CRCW04021M18FKED | Resistor | 1.18M | CRCW04021M18FKED | R_0402_1005Metric | 1
286 | R49 | RC0402JR-071M2L | Resistor | 1.2M | RC0402JR-071M2L | R_0402_1005Metric | 1
287 | R50 | CRCW04021M60FKEDC | Resistor | 1.6M | CRCW04021M60FKEDC | R_0402_1005Metric | 1
288 | R5 |  | Resistor | NC |  |  | 1
289 | R66 |  | Resistor | NC |  |  | 1
290 | R67 |  | Resistor | NC |  |  | 1
291 | R69 |  | Resistor | NC |  |  | 1
292 | R70 |  | Resistor | NC |  |  | 1
293 | R71 |  | Resistor | NC |  |  | 1
294 | R83 |  | Resistor | NC |  |  | 1
295 | R87 |  | Resistor | NC |  |  | 1
296 | R89 |  | Resistor | NC |  |  | 1
297 | R90 |  | Resistor | NC |  |  | 1
298 | R91 |  | Resistor | NC |  |  | 1
299 | RN1 | CAT16-2701F4LF | 4 resistor network, parallel topology, SIP package | CAT16-2701F4LF | CAT16-2701F4LF | R_Cat16-4 | 1
300 | S1 | SKRHACE010 |  | SKRHACE010 | SKRHACE010 | SKRHAAE010 | 1
301 | U5 | ADS1114IDGSR | ADC | ADS1114IDGSR | ADS1114IDGSR | SOP50P490X110-10N | 1
302 | U15 | B39162B9415K610 | B39162B9415K610 | B39162B9415K610 | B39162B9415K610 | B39162B9415K610 | 1
303 | U14 | BGU8009,115 | BGU8009 | BGU8009,115 | BGU8009,115 | BGU8009,115 | 1
304 | U3 | LP3874EMPX-3.3/NOPB |  | LP3874EMP-3.3_NOPB | LP3874EMPX-3.3/NOPB | SOT-223-5 | 1
305 | U6 | MAX6070AAUT30+T |  | MAX6070AAUT30+T | MAX6070AAUT30+T | SOT-23-6 | 1
306 | U2 | MCP1501T-33E/CHY |  | MCP1501T-33E_CHY | MCP1501T-33E/CHY | SOT-23-6 | 1
307 | U13 | NXB0108BQ-Q100X |  | NXB0108 | NXB0108BQ-Q100X | WQFN-20-1EP_2.5x4.5mm_P0.5mm_EP1x2.9mm | 1
308 | U9 |  |  | OLED_2.49" |  |  | 1
309 | U17 | PI5C3257ZHDEX |  | PI5C3257 | PI5C3257ZHDEX | QFN-16-1EP_3x3mm_P0.5mm_EP1.7x1.7mm | 1
310 | U18 | PI5C3257ZHDEX |  | PI5C3257 | PI5C3257ZHDEX | QFN-16-1EP_3x3mm_P0.5mm_EP1.7x1.7mm | 1
311 | U8 | S2-108HB-Z308J |  | SIM7080G | S2-108HB-Z308J | XCVR_SIM7080G | 1
312 | U12 | SN74HCS02QPWRQ1 | Logic Gates | SN74HCS02-Q1 | SN74HCS02QPWRQ1 | TSSOP-14_4.4x5mm_P0.65mm | 1
313 | U4 | TLV3202AID | Dual operational amplifier | TLV3202AID | TLV3202AID | SOIC-8_3.9x4.9mm_P1.27mm | 1
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

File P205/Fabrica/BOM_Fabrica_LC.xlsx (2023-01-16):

# | References | Manufacturer_Part_Number | Description | Value | Footprint | Qnt
1 | C110 | CL05C120JB51PNC | Unpolarized capacitor | 12p | C_0402_1005Metric | 8
2 | C119 | CL05C221JB51PNC | Unpolarized capacitor | 220p | C_0402_1005Metric | 6
3 | C125 | C0402C103K5RAC7411 | Unpolarized capacitor | 10n | C_0402_1005Metric | 14
4 | C1 | GCM155R71H104KE02D | Unpolarized capacitor | 100n | C_0402_1005Metric | 35
5 | C89 | C1005X5R1E474K050BB | Unpolarized capacitor | 0.47u | C_0402_1005Metric | 3
6 | C100 | GRT155R61E105KE01D | Unpolarized capacitor | 1u | C_0402_1005Metric | 23
7 | C106 | TMK212BBJ106MG-T | Unpolarized capacitor | 10u | C_0805_2012Metric | 15
8 | D1 | DESD5V0U1BA-7 | Bidirectional transient-voltage-suppression diode | DESD5V0U1BA-7 | D_SOD-323 | 27
9 | D14 | FML340A-W | Schottky diode | FML340A-W | D_SMA | 6
10 | IC6 | 23K640-I/ST | Microchip Technology SRAM, 23K640-I/ST- 64kbit | 23K640-I_ST | SOP65P640X120-8N | 1
11 | IC1 | ADS1296RIZXGT | 6-Channel, 24-Bit Analog-To-Digital Converter w/Integrated Respiration | ADS1296RIZXGT | BGA64C80P8X8_800X800X145 | 1
12 | IC2 | ADS1298IPAG | 8-Channel 24-bit ADC With Integrated ECG Front End | ADS1298IPAG | QFP50P1200X1200X120-64N | 1
13 | IC3 | BQ51050BRHLR | Qi (WPC) Compliant Highly Integrated Secondary-Side Direct Lithium Ion Charger. | BQ51050BRHLR | BQ51050BRHLR | 1
14 | IC4 | SN74HCS00QPWRQ1 | Logic Gates | SN74HCS00QPWRQ1 | SOP65P640X120-14N | 1
15 | J14 | 12401598E4#2A |  | USB-C | AMPHENOL_12401598E4#2A | 1
16 | J2 | M40-4010446 |  | Batt | M404010446 | 1
17 | J1 | MEM2061-01-188-00-A | MEM2061 Series 8 Position 1.1 mm Pitch Push-Push MicroSD SMT Memory Card Connector | MEM2061-01-188-00-A | MEM20610118800A | 1
18 | J10 | SIM8051-6-0-14-00-A | SIM Card | SIM_Card | SIM8051601401A | 1
19 | J12 | U.FL-R-SMT-1(10) |  | U.FL-R-SMT-1(10) | CONUFL001-SMD | 3
20 | L2 | 7447840115 | Inductor | 15n | L_0402_1005Metric | 2
21 | Q1 | DMG2305UX-7 | MOSFET P-Ch 20V 5A Enhancement SOT23 Diodes | DMG2305 | SOT-23 | 4
22 | R36 | SFR01MZPJ000 | Resistor | 0 | R_0402_1005Metric | 9
23 | R103 | CRCW0402330RJNEDHP | Resistor | 330 | R_0402_1005Metric | 8
24 | R1 | SG73P1ETTP512J | Resistor | 5.1k | R_0402_1005Metric | 11
25 | R101 | RC0402JR-7W10KL | Resistor | 10k | R_0402_1005Metric | 17
26 | R26 | RCS04021M00FKED | Resistor | 1M | R_0402_1005Metric | 13
27 | U5 | ADS1114IDGSR | ADC | ADS1114IDGSR | SOP50P490X110-10N | 1
28 | U15 | B39162B9415K610 | B39162B9415K610 | B39162B9415K610 | B39162B9415K610 | 1
29 | U14 | BGU8009,115 | BGU8009 | BGU8009,115 | BGU8009,115 | 1
30 | U13 | NXB0108BQ-Q100X |  | NXB0108 | WQFN-20-1EP_2.5x4.5mm_P0.5mm_EP1x2.9mm | 1
31 | U17 | PI5C3257ZHDEX |  | PI5C3257 | QFN-16-1EP_3x3mm_P0.5mm_EP1.7x1.7mm | 2
32 | U8 | S2-108HB-Z308J |  | SIM7080G | XCVR_SIM7080G | 1
33 | U12 | SN74HCS02QPWRQ1 | Logic Gates | SN74HCS02-Q1 | TSSOP-14_4.4x5mm_P0.65mm | 1
34 | U1 | TLV9062QDGKRQ1 | Dual operational amplifier | TLV9062QDGKRQ1 | VSSOP-8_3.0x3.0mm_P0.65mm | 1
35 | U7 | nRF52832-QFAB-R |  | nRF52832 | QFN-48-1EP_6x6mm_P0.4mm_EP4.6x4.6mm | 2
36 | X1 | ECS-.327-12.5-12R-TR | Crystals 32.768kHz 12.5pF -40C +85C | ECS-.327-12.5-12R-TR | ECS32712512RTR | 2
37 | X3 | ECS-.327-12.5-12R-TR | Crystals 32.768kHz 12.5pF -40C +85C | ECS-.327-12.5-12R-TR | ECS32712512RTR | 1
38 | X2 | ECS-320-8-37B-7KM-TR | Crystals 32MHz 8pf 50 ohms -20C to 70C 7ppm | ECS-320-8-37B-7KM-TR | ECS320837B7KMTR | 1
39 | Y1 | SR4G008 | Antennas 1559-1609MHz Avg. Eff >75% Linear | SR4G008 | SR4G008 | 1
40 | Z1 | BQ25300RTER | Battery Management Standalone 1-cell, 17-V, 3.0-A battery charger 16-WQFN | BQ25300RTER | QFN50P300X300X80-17N-D | 1
Total: | 230

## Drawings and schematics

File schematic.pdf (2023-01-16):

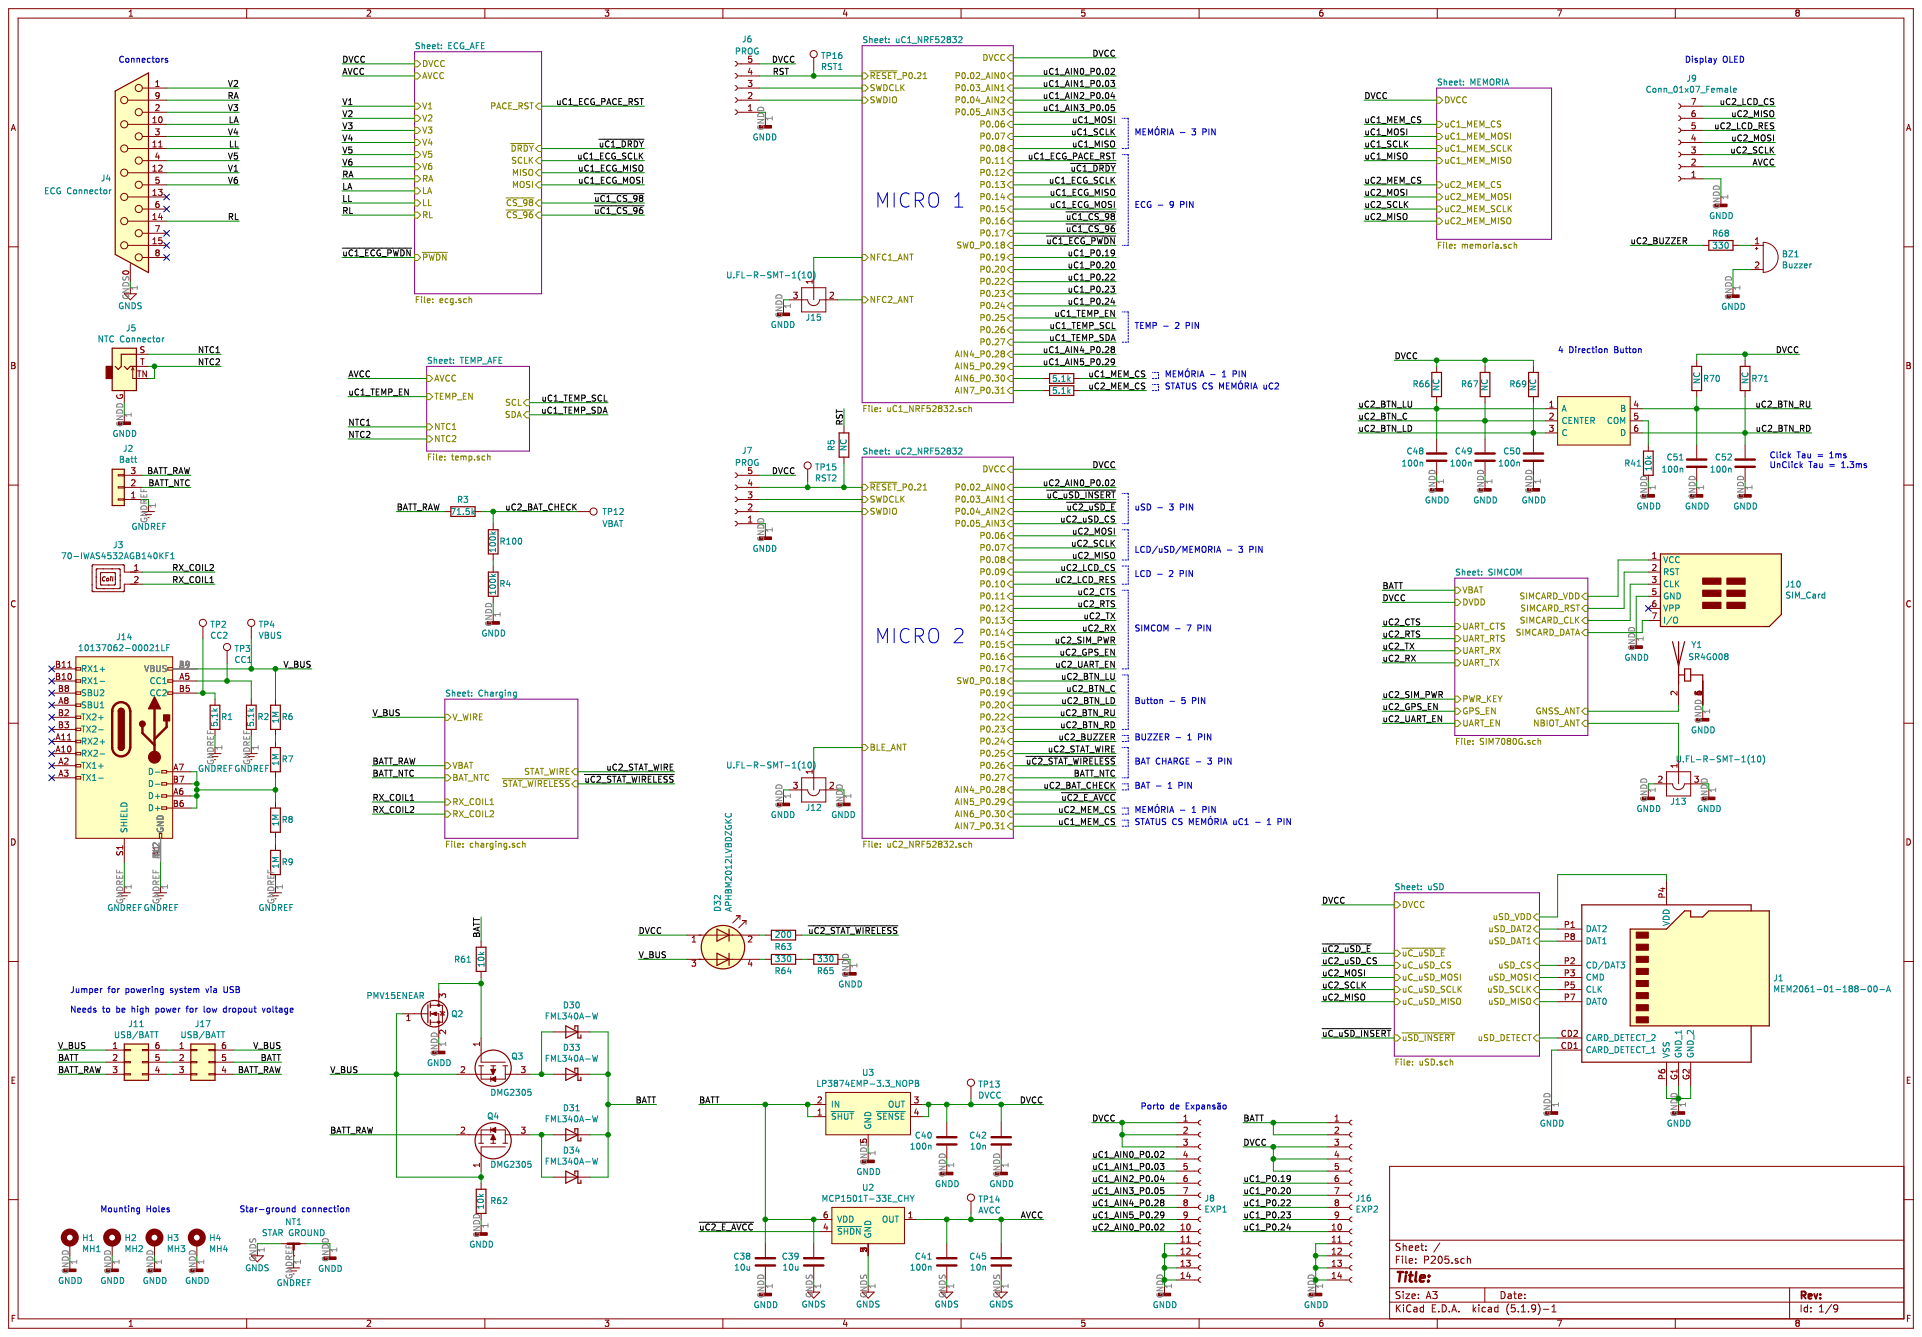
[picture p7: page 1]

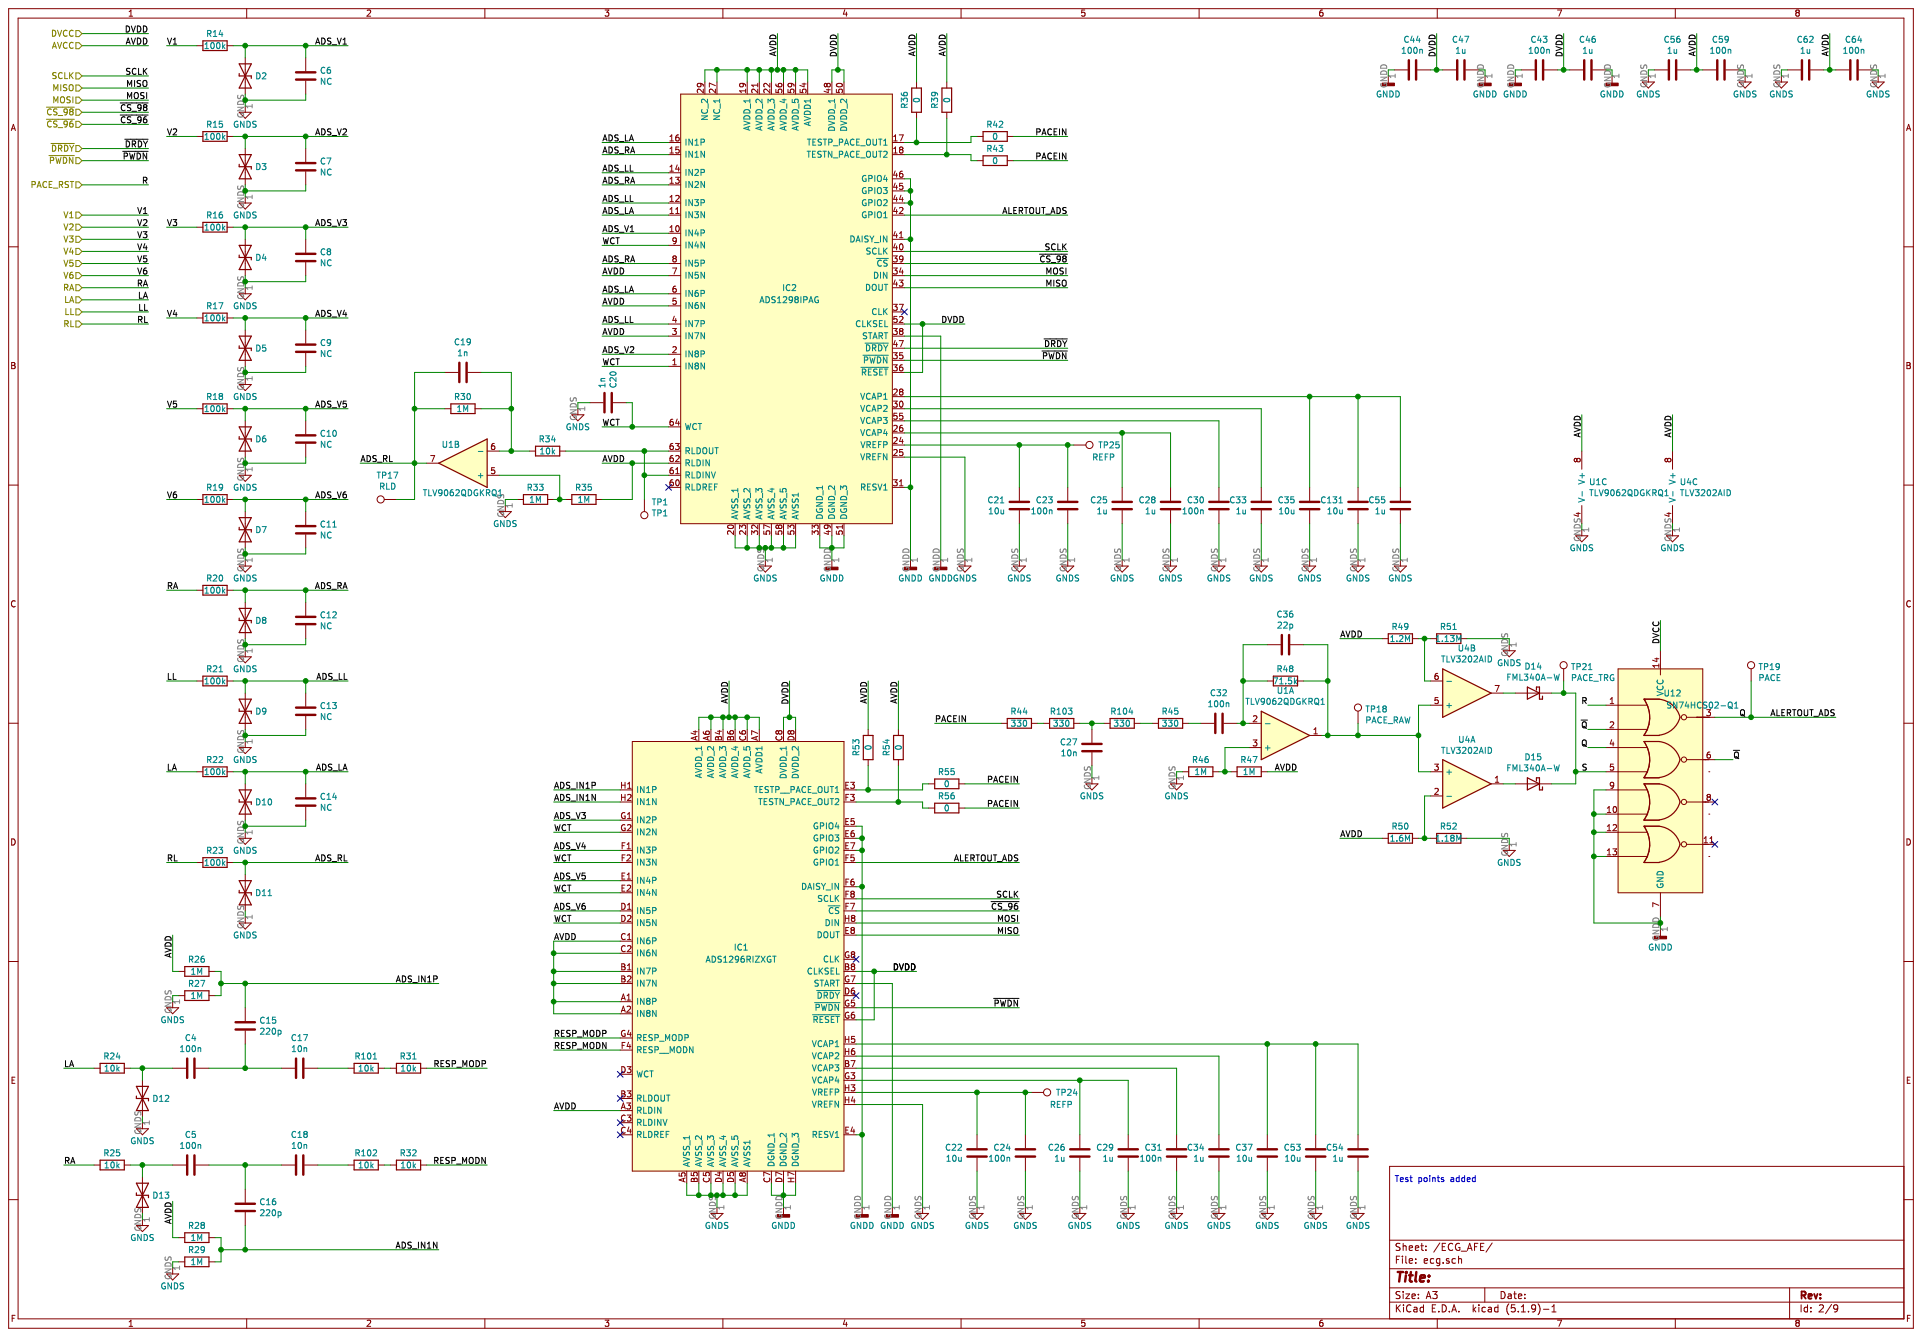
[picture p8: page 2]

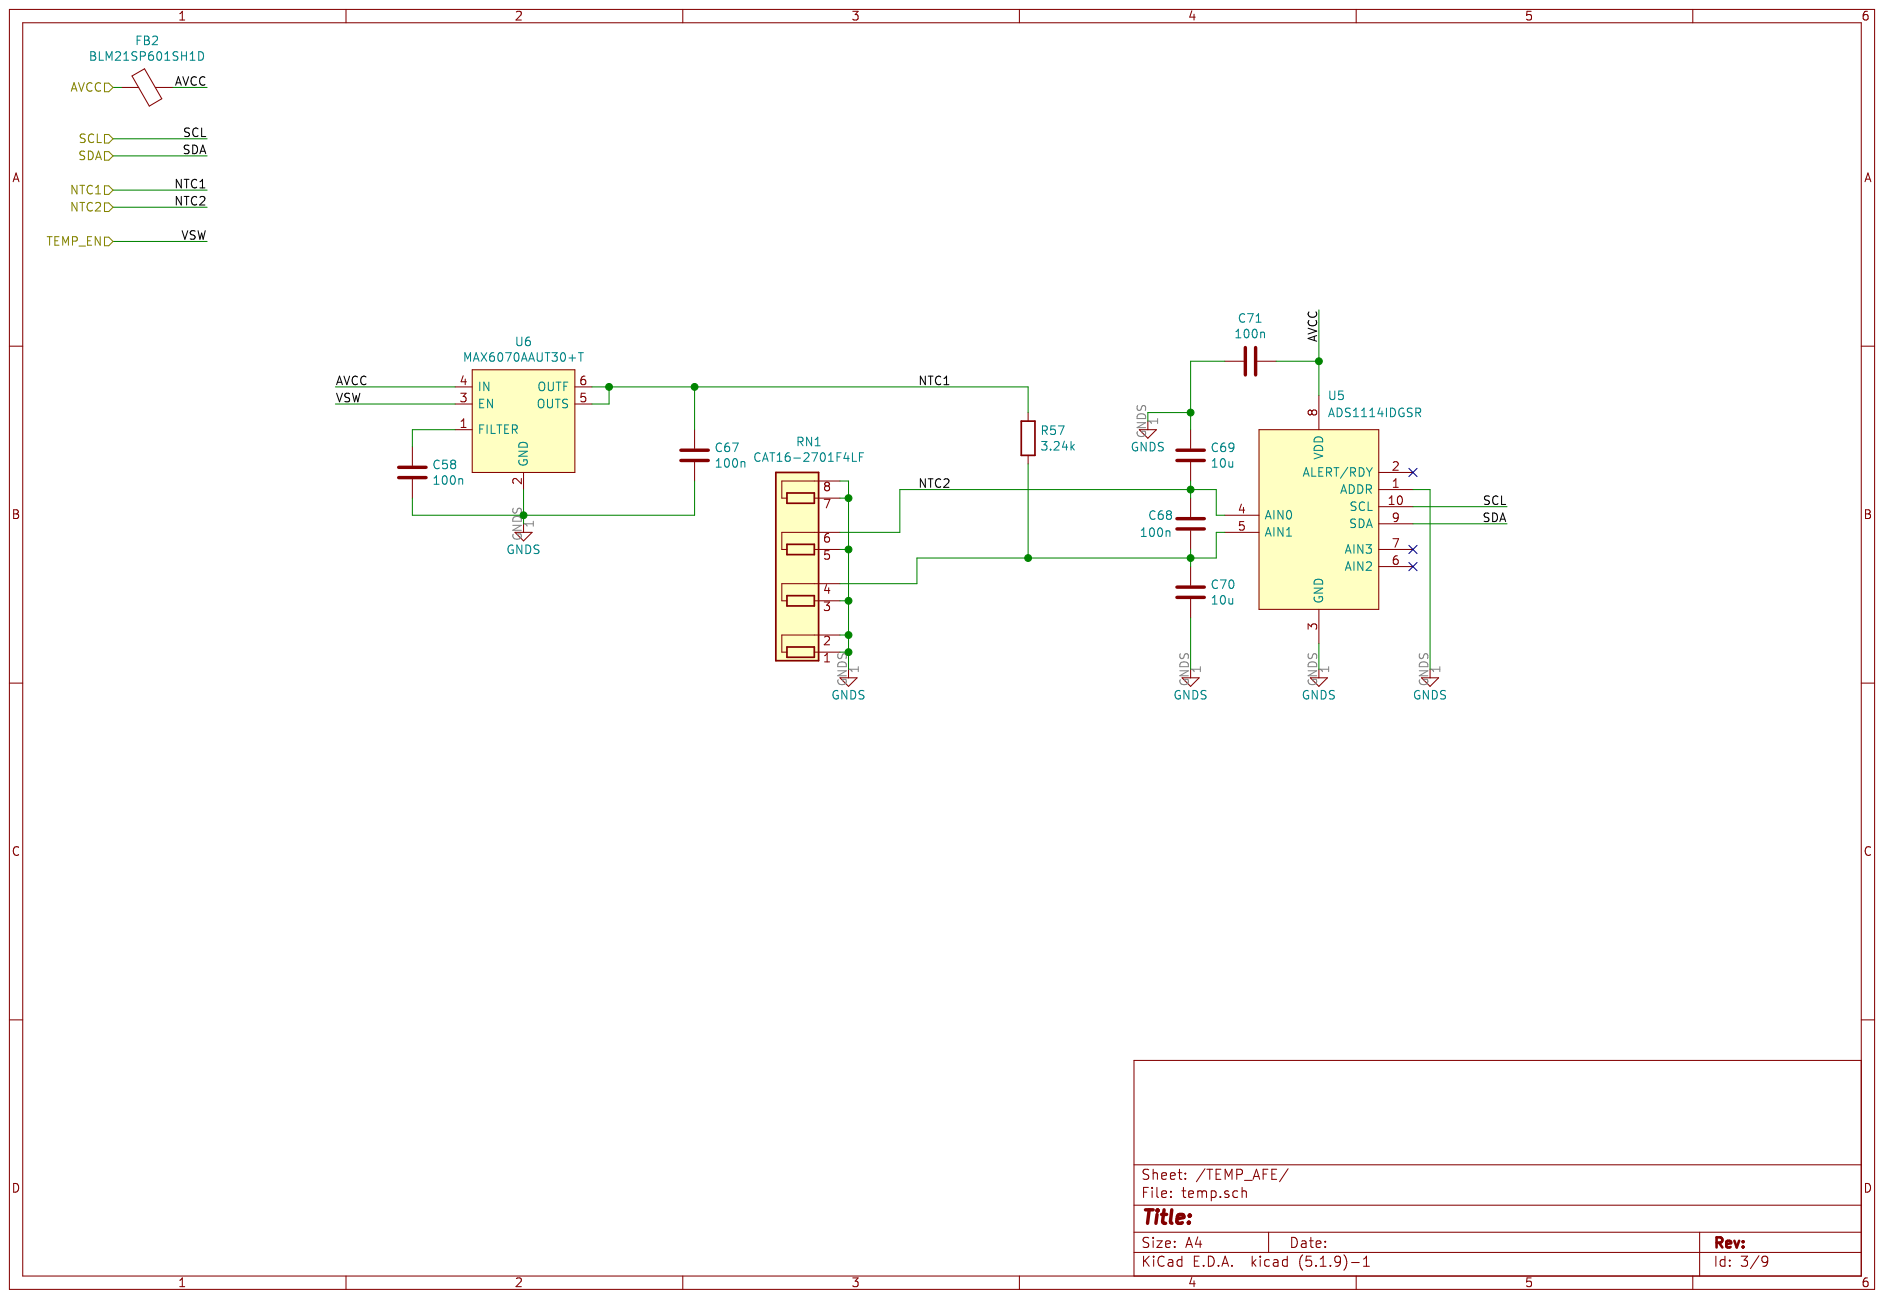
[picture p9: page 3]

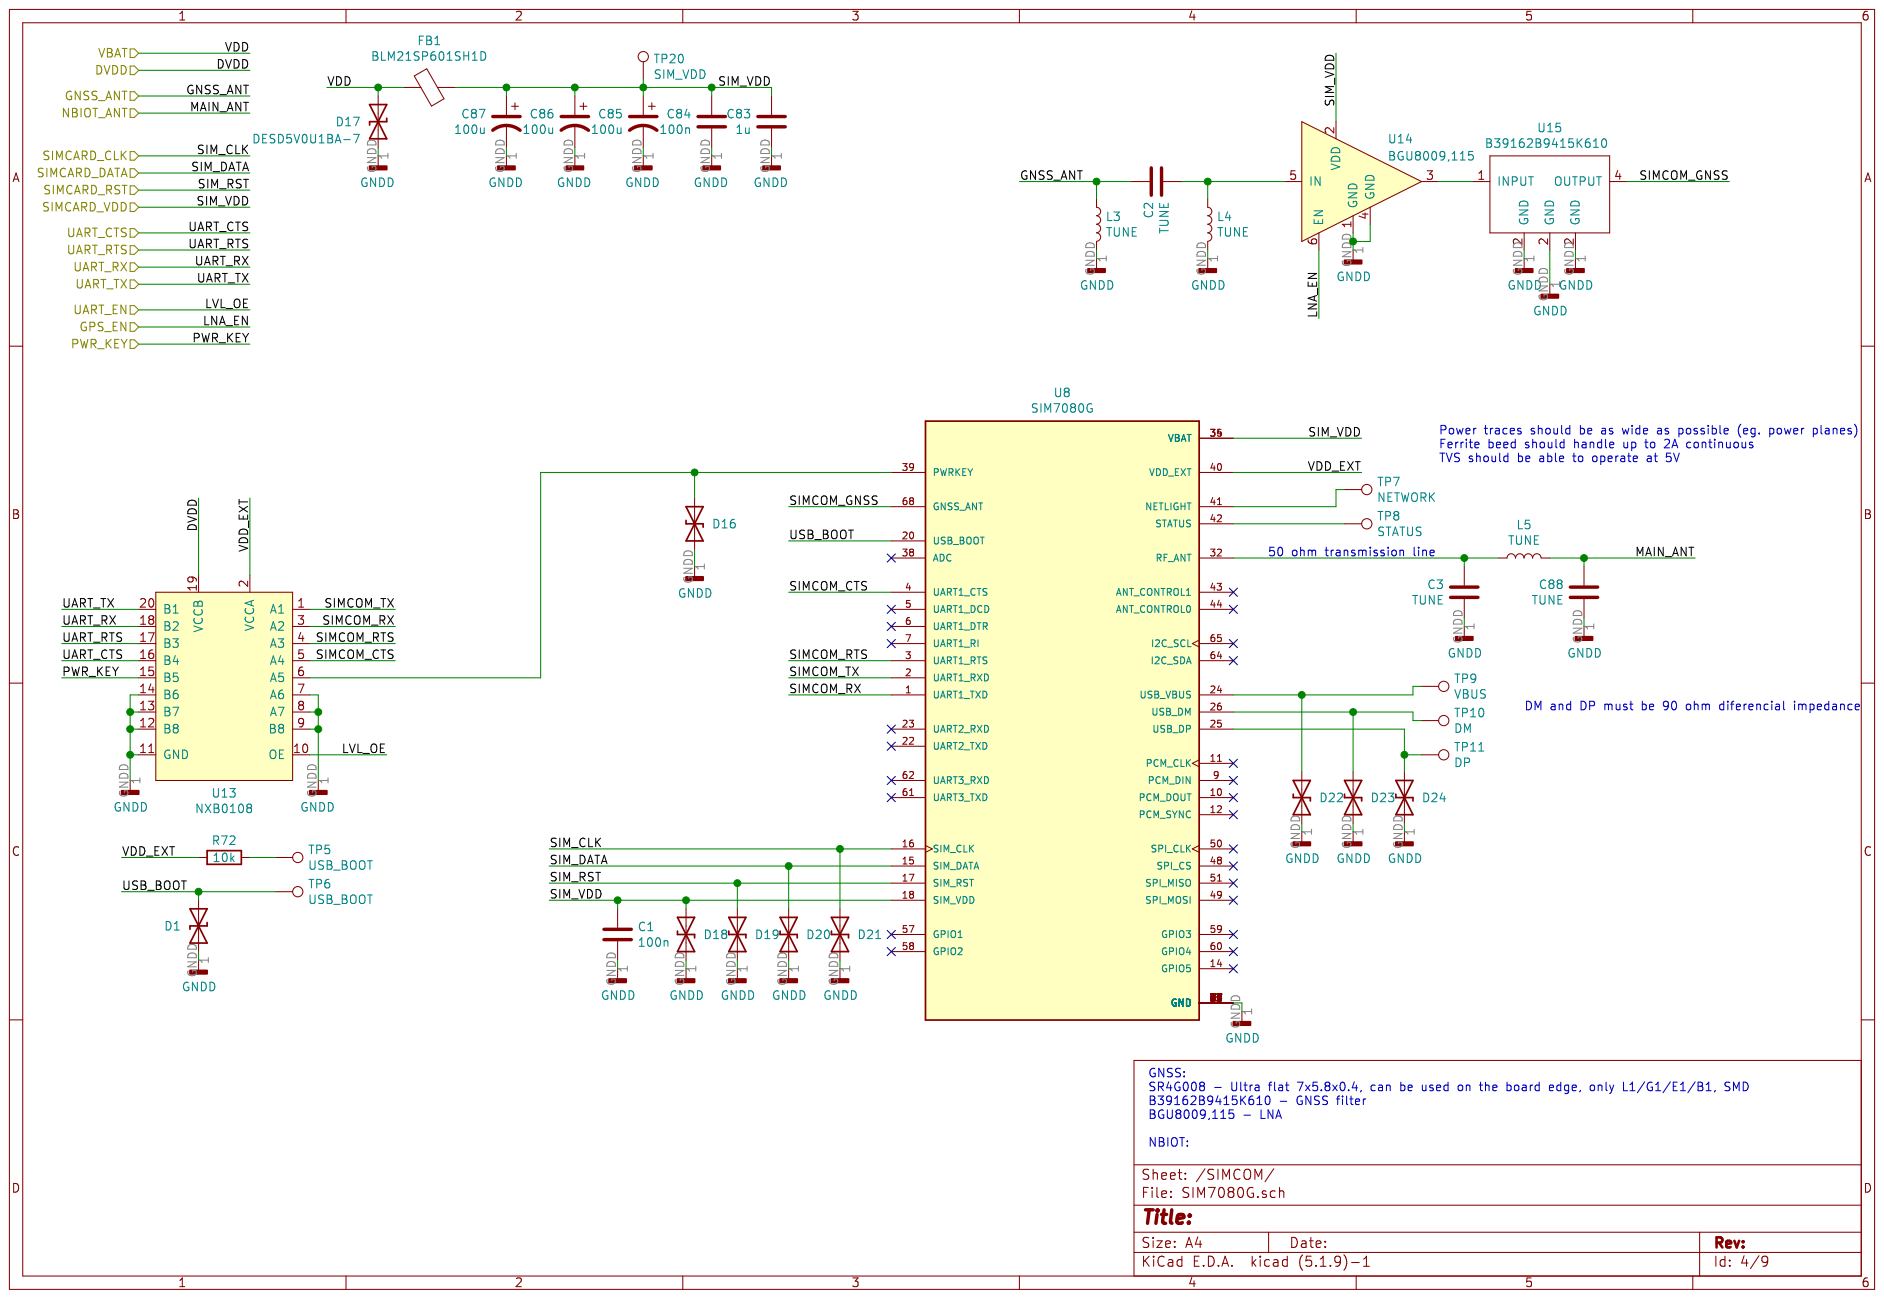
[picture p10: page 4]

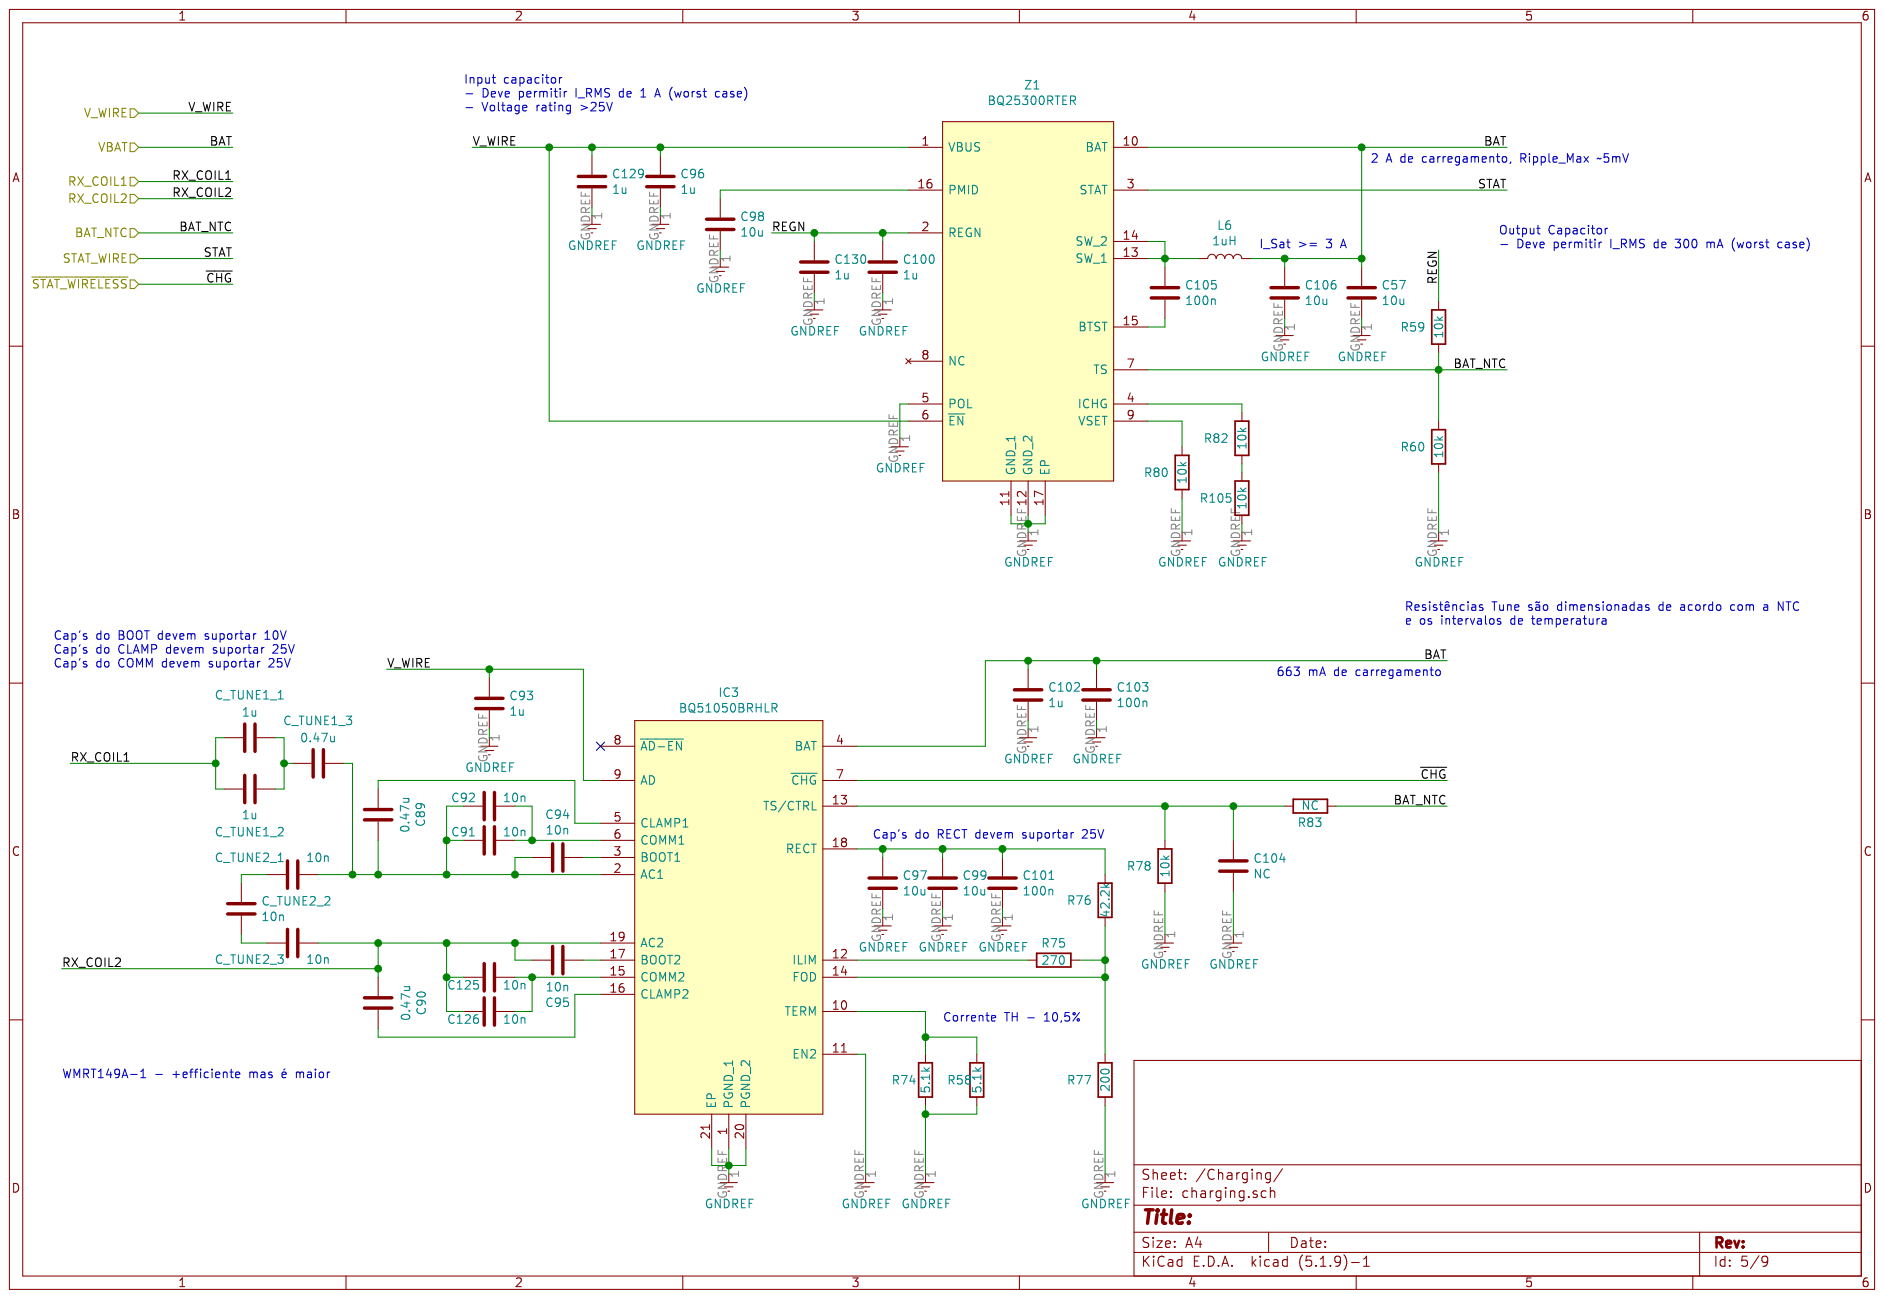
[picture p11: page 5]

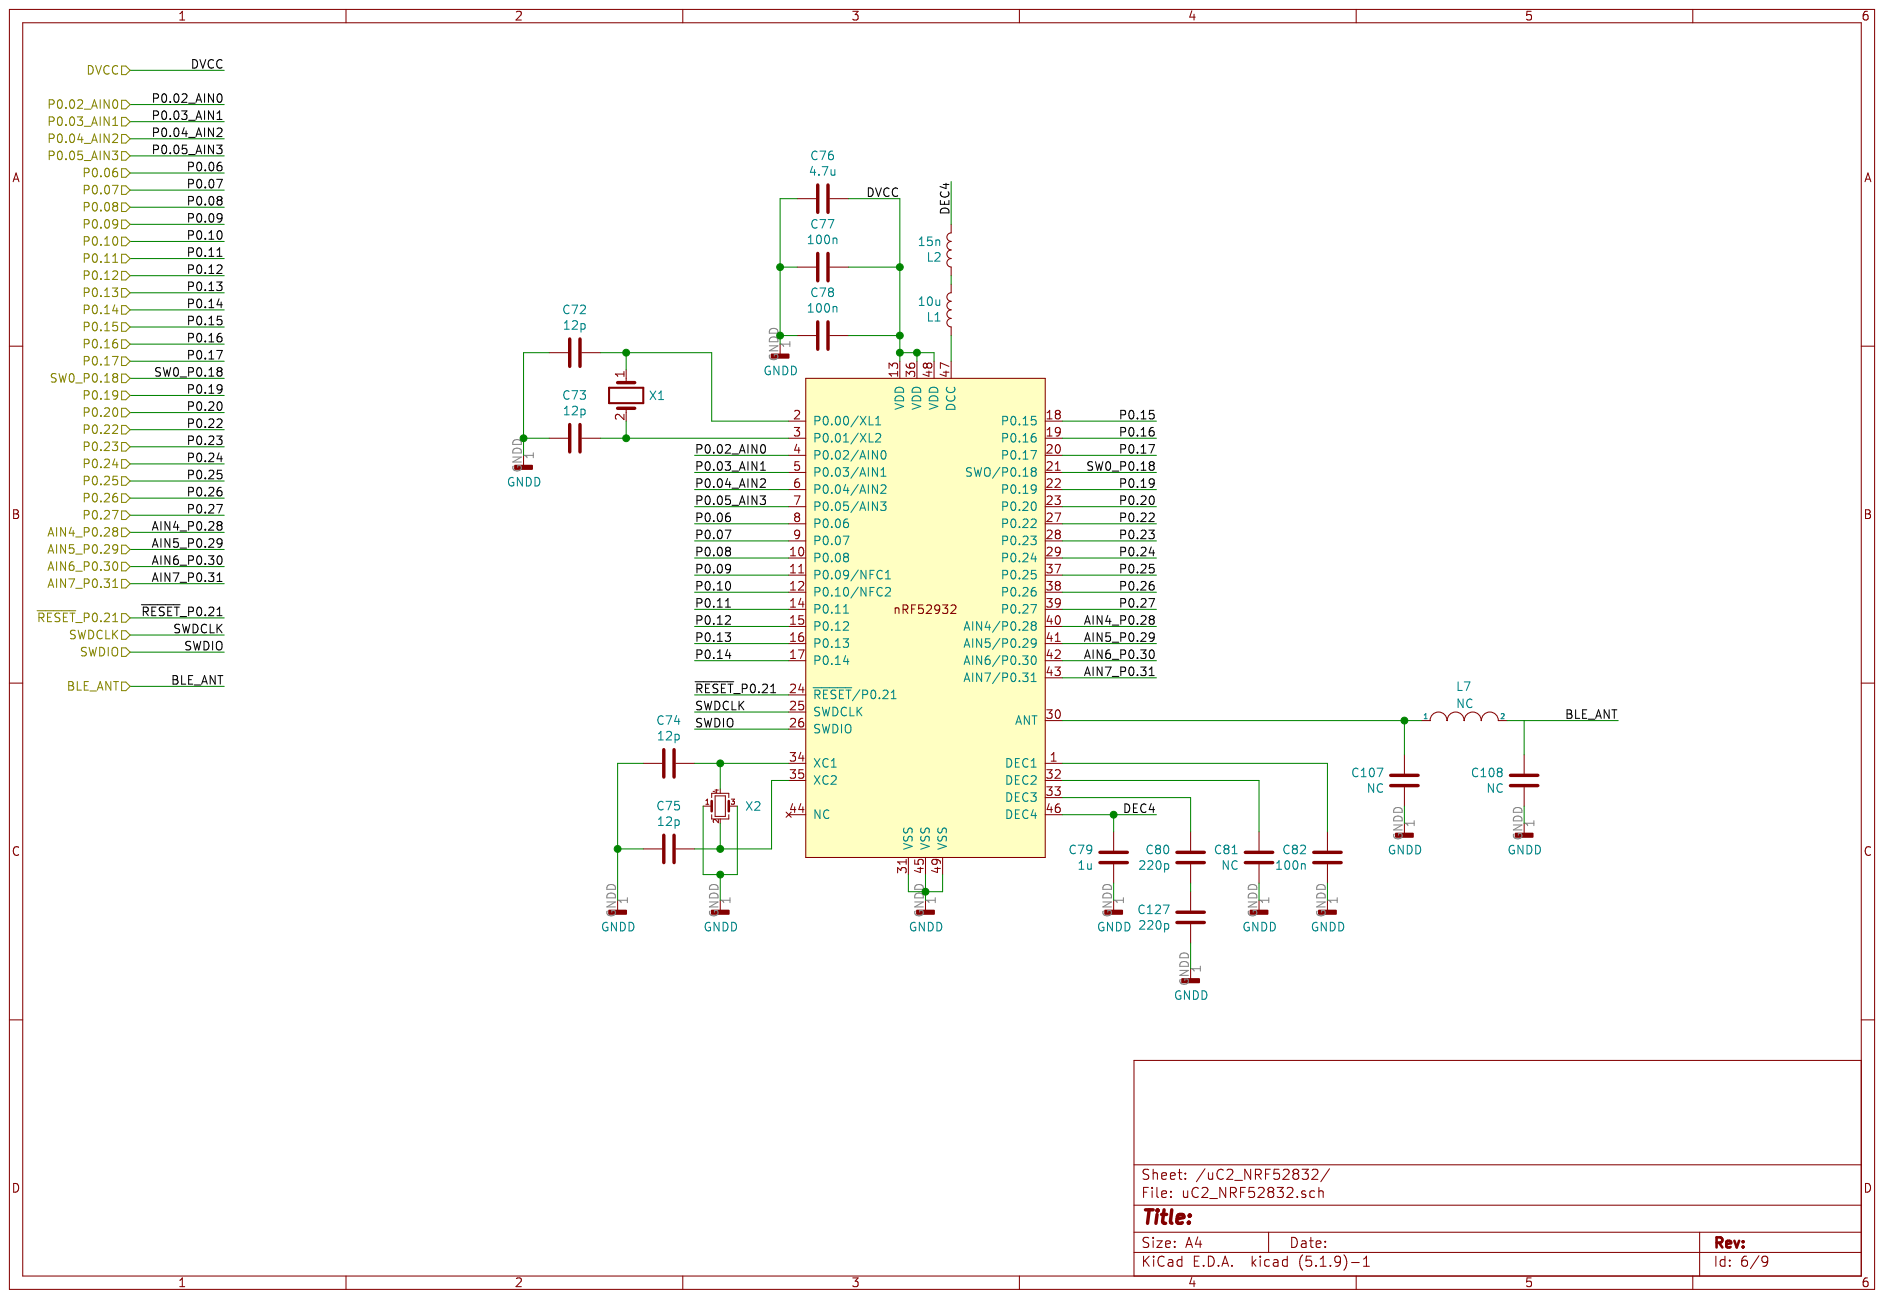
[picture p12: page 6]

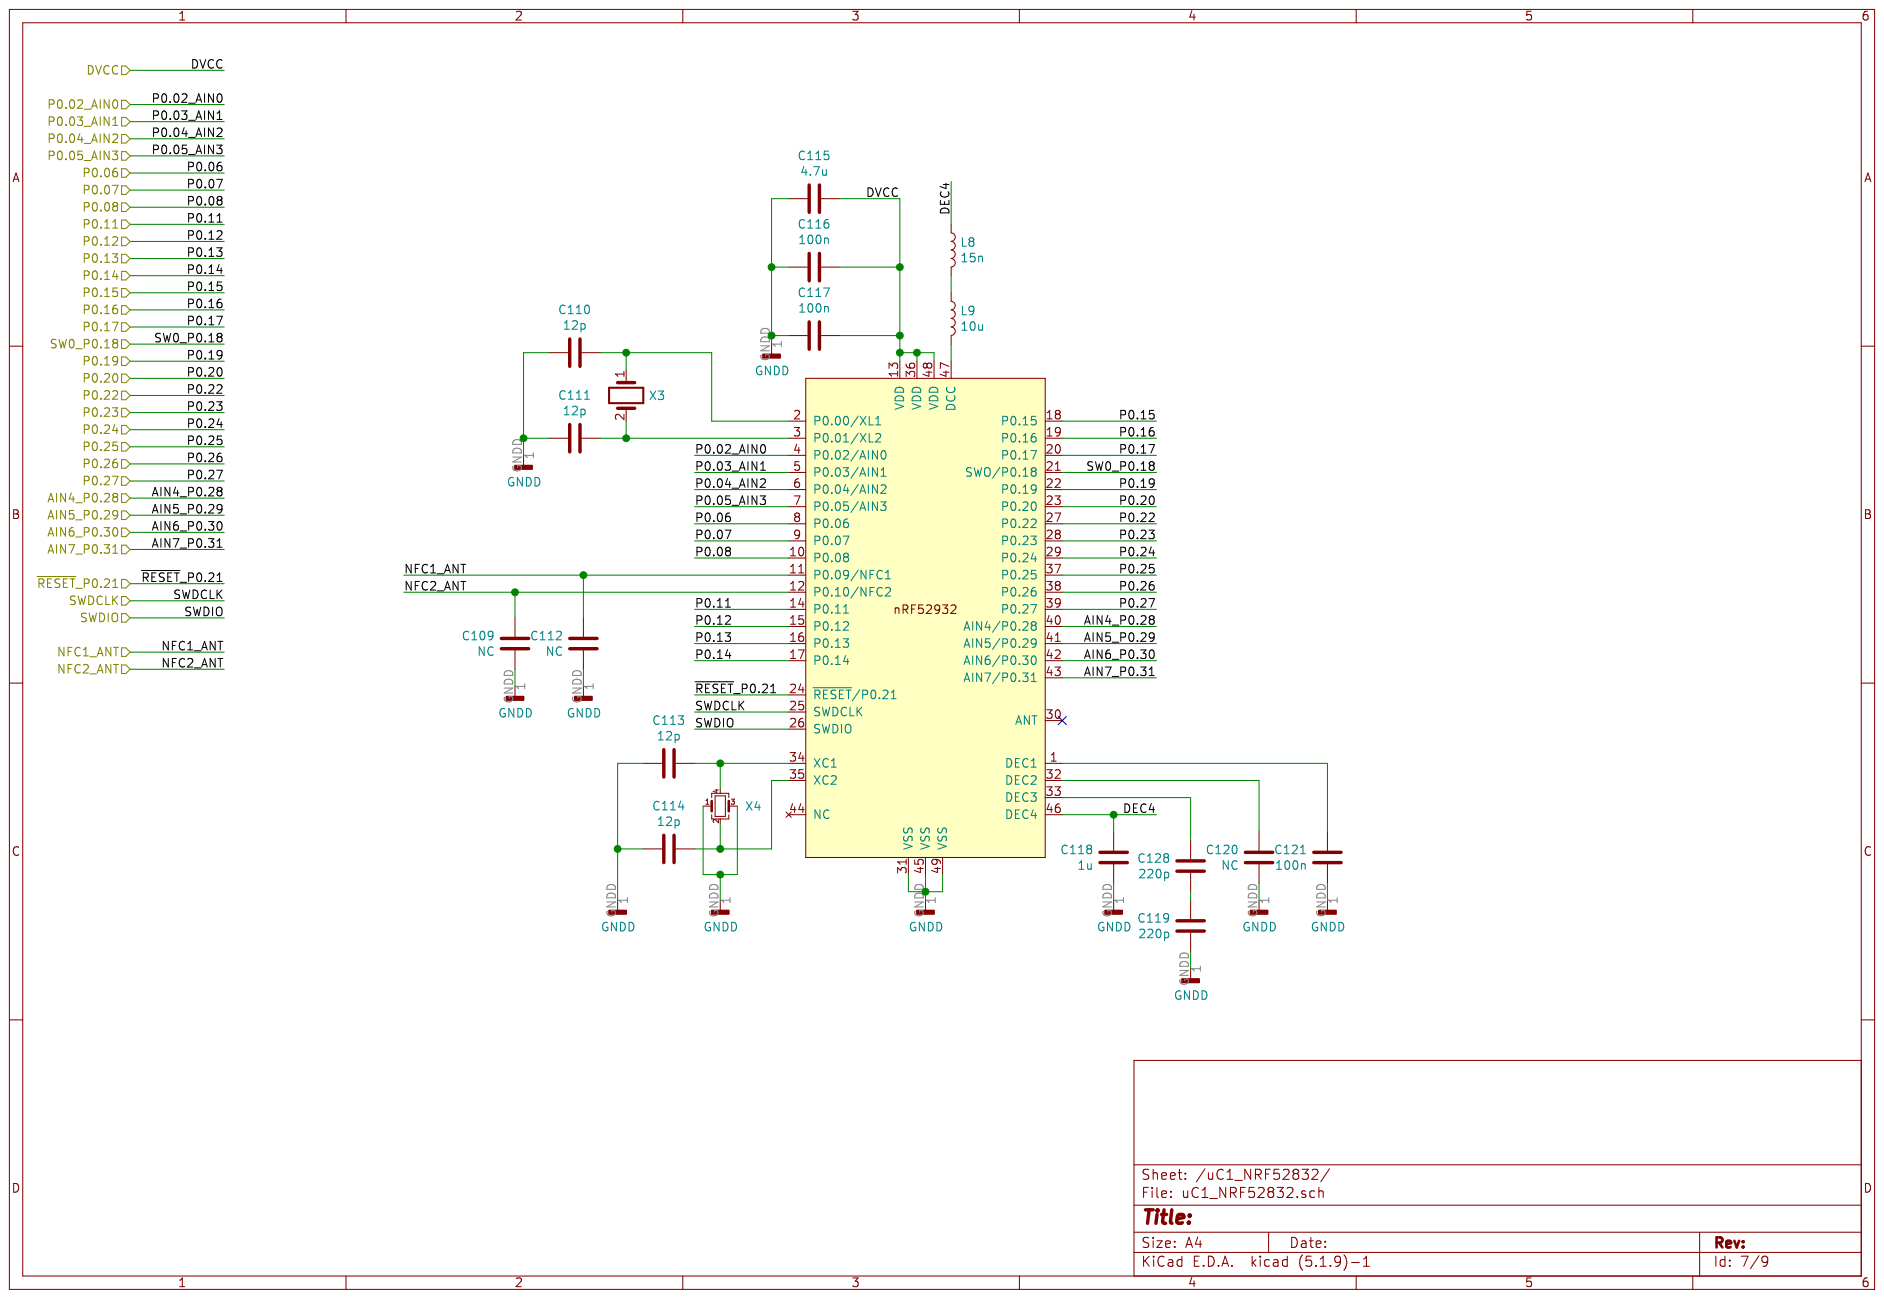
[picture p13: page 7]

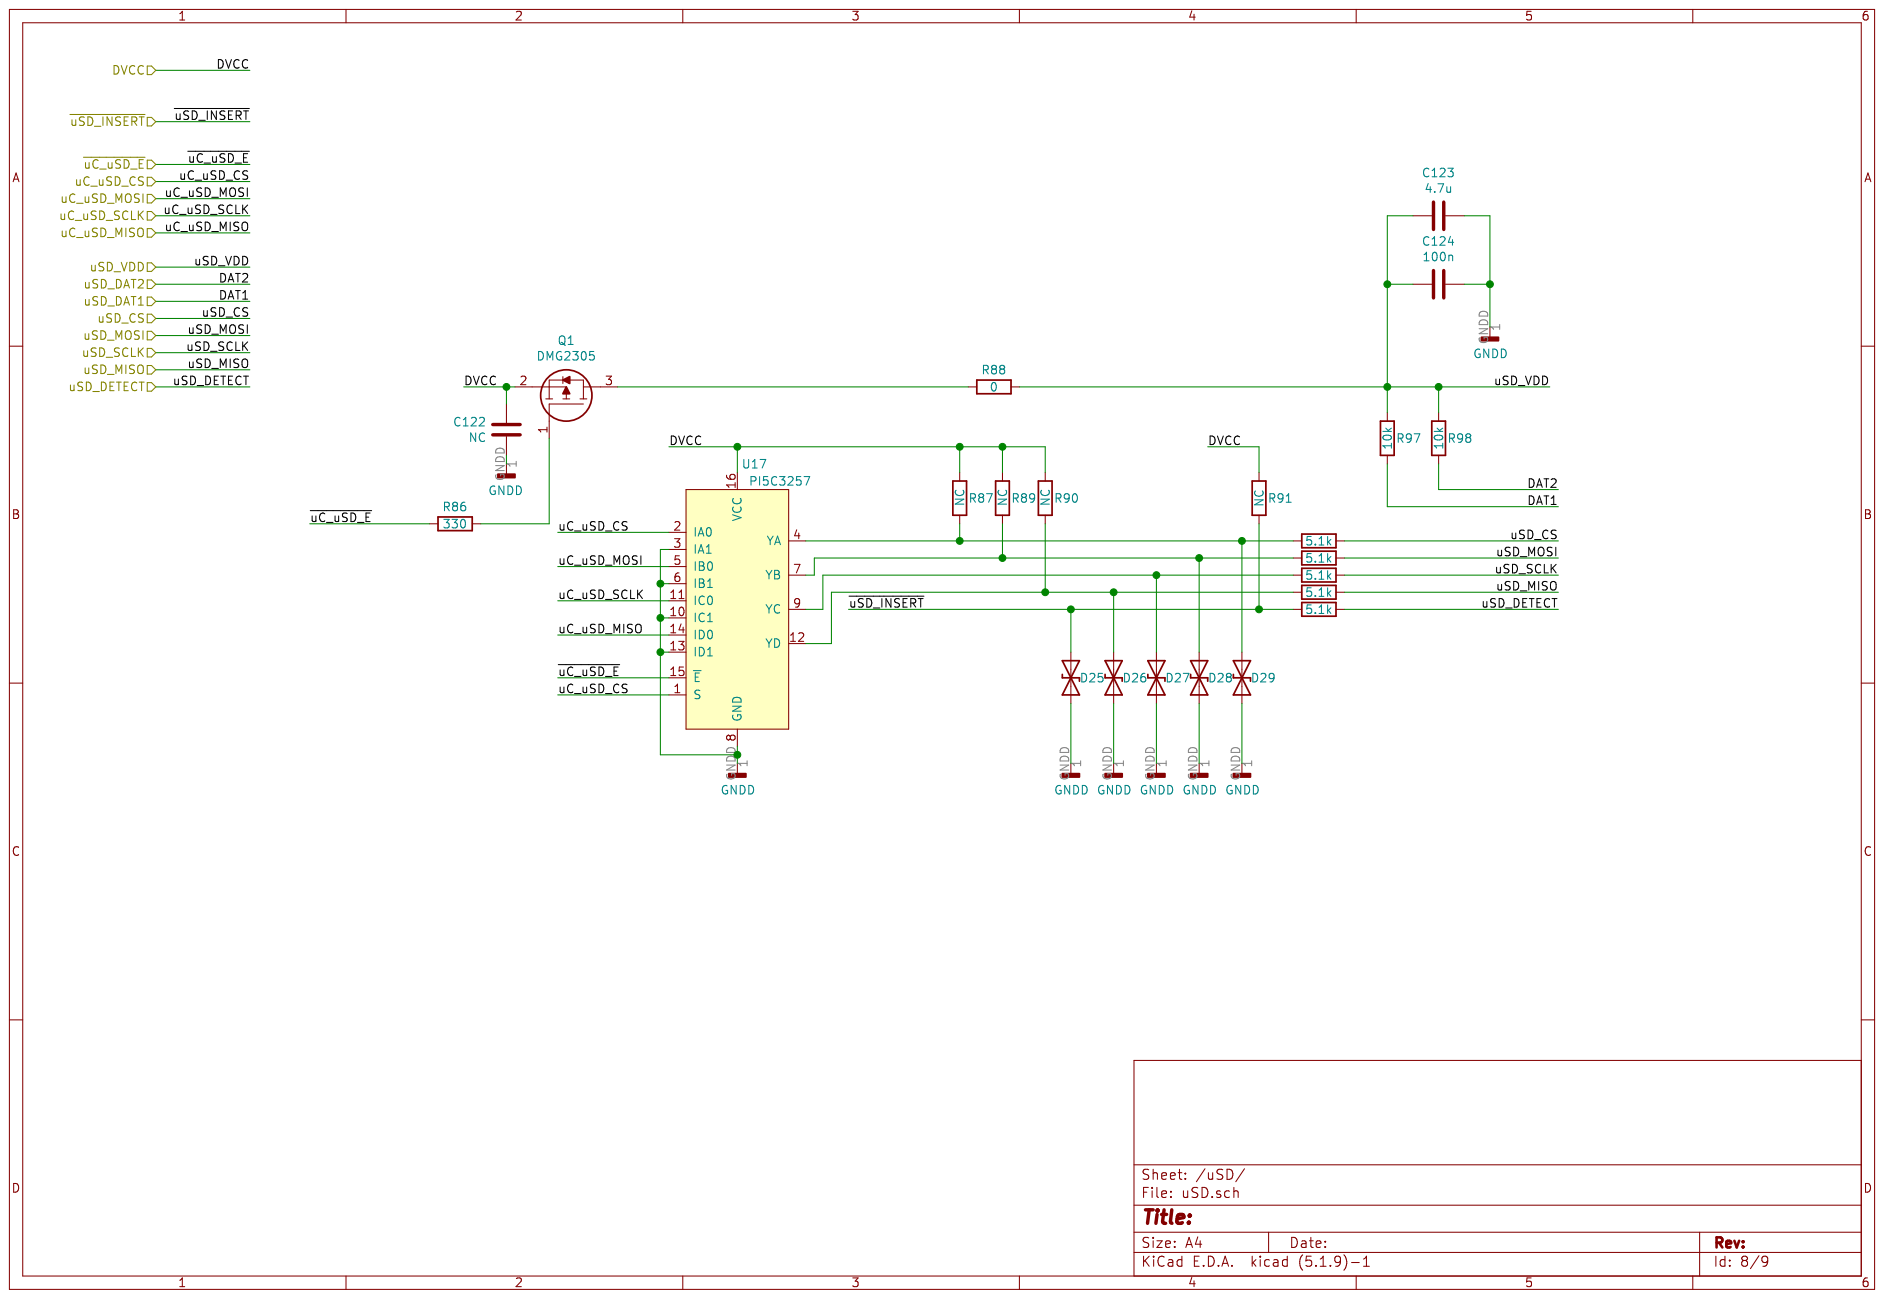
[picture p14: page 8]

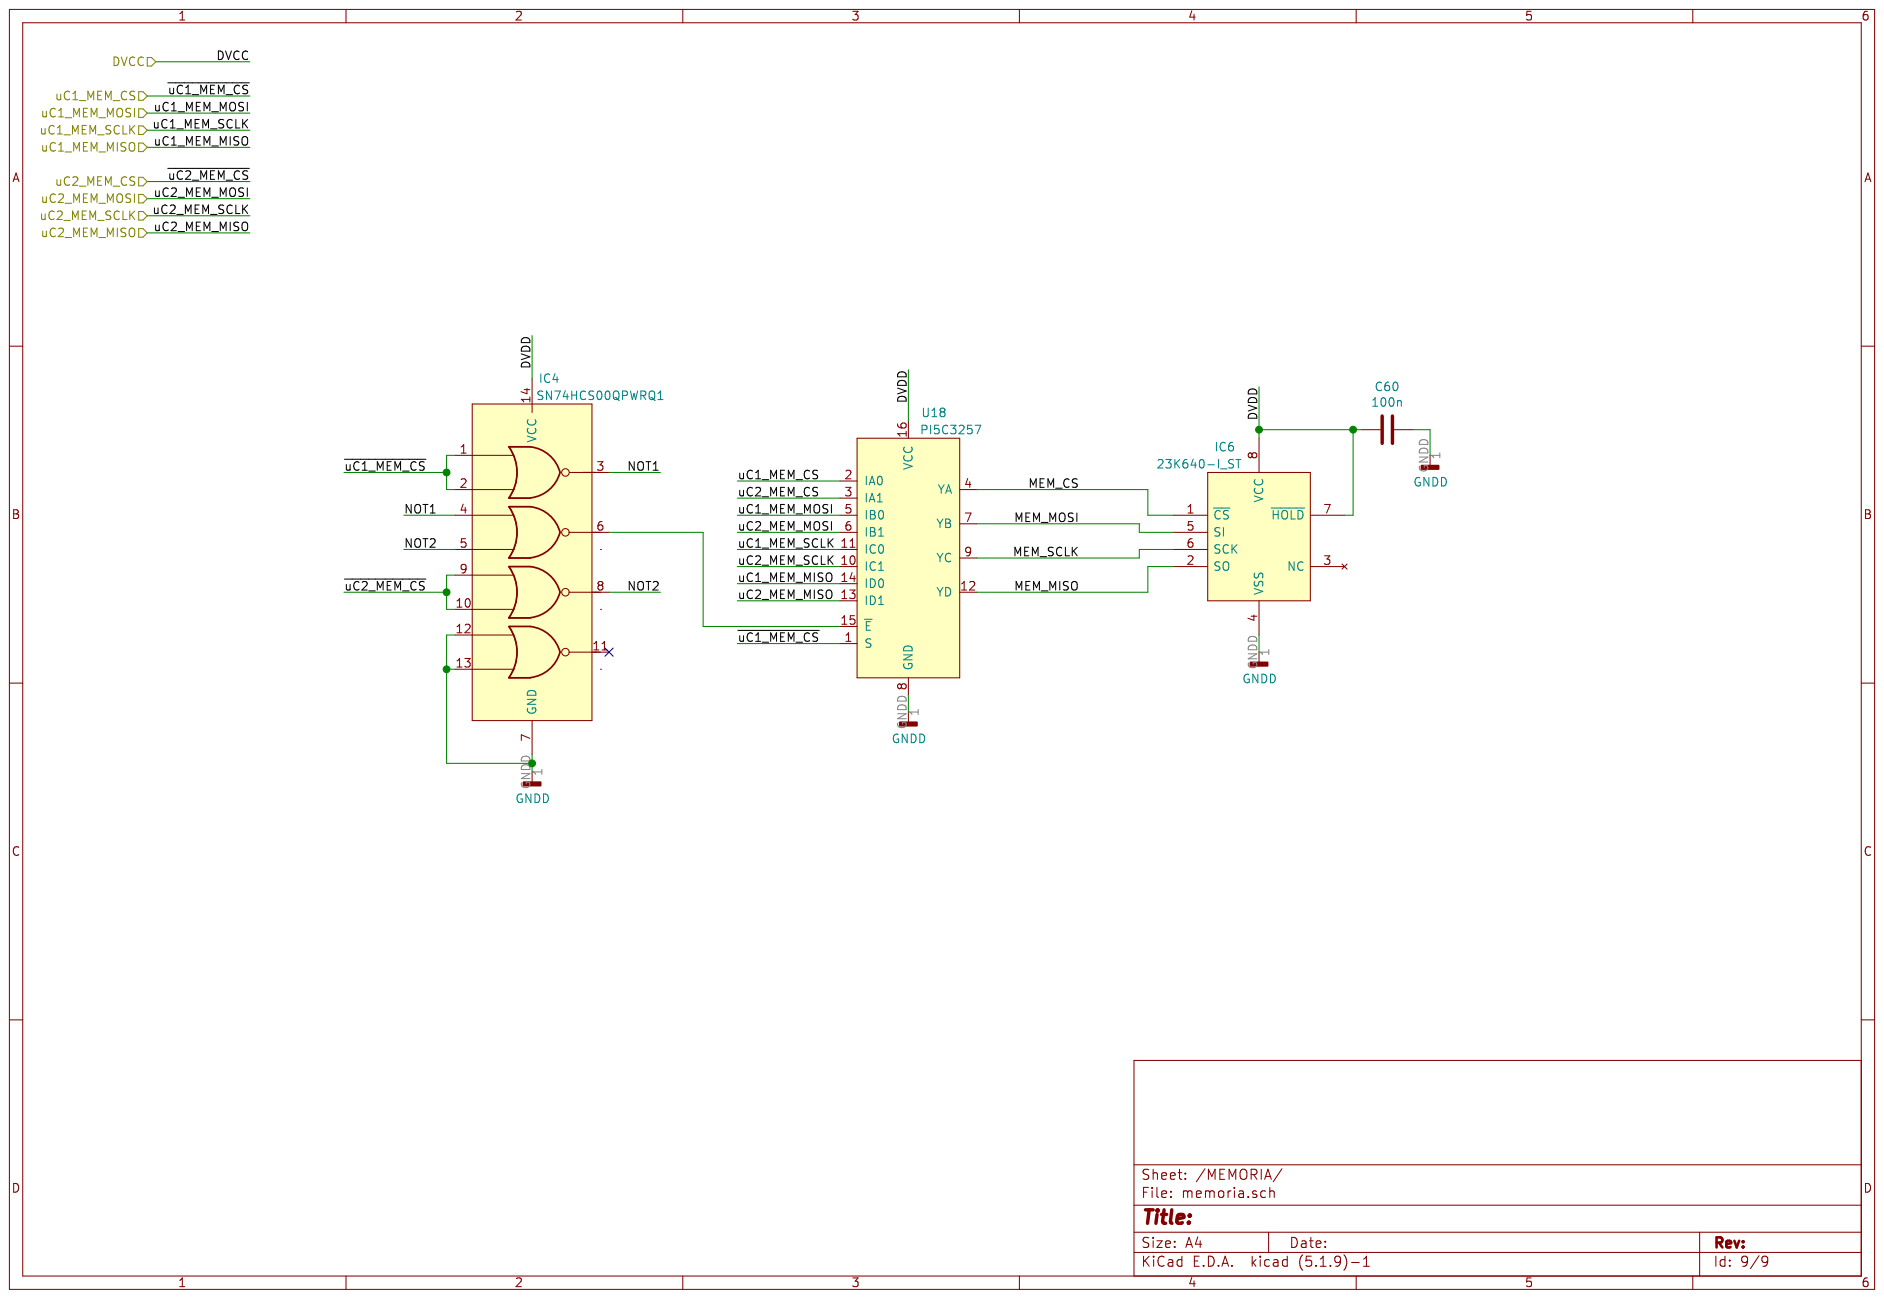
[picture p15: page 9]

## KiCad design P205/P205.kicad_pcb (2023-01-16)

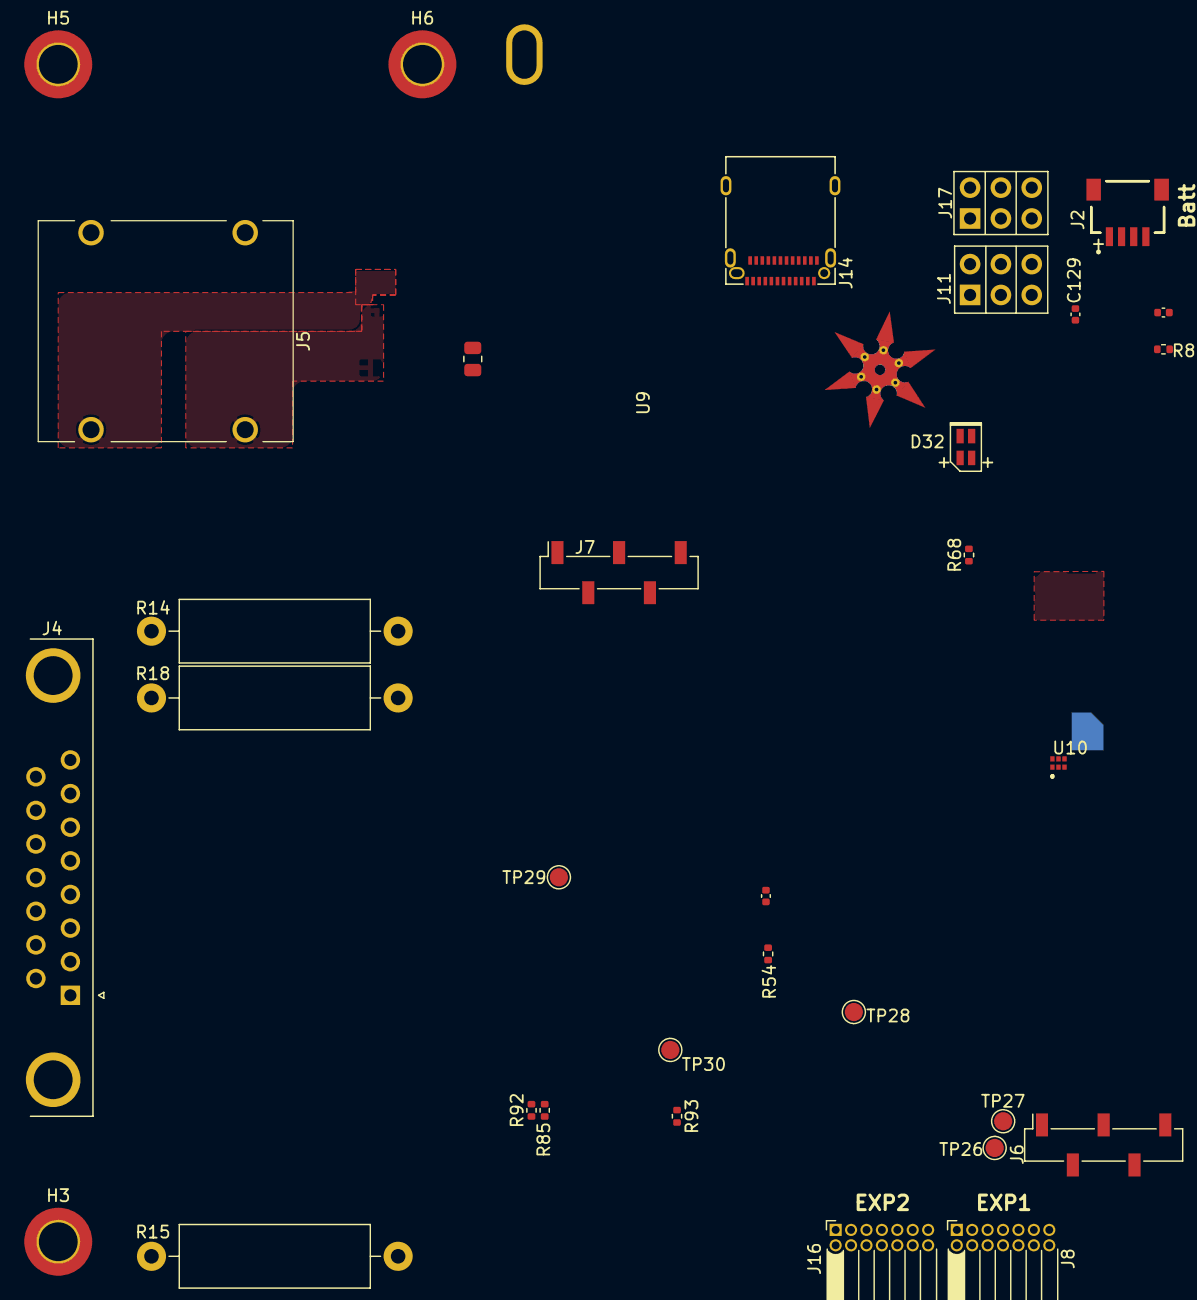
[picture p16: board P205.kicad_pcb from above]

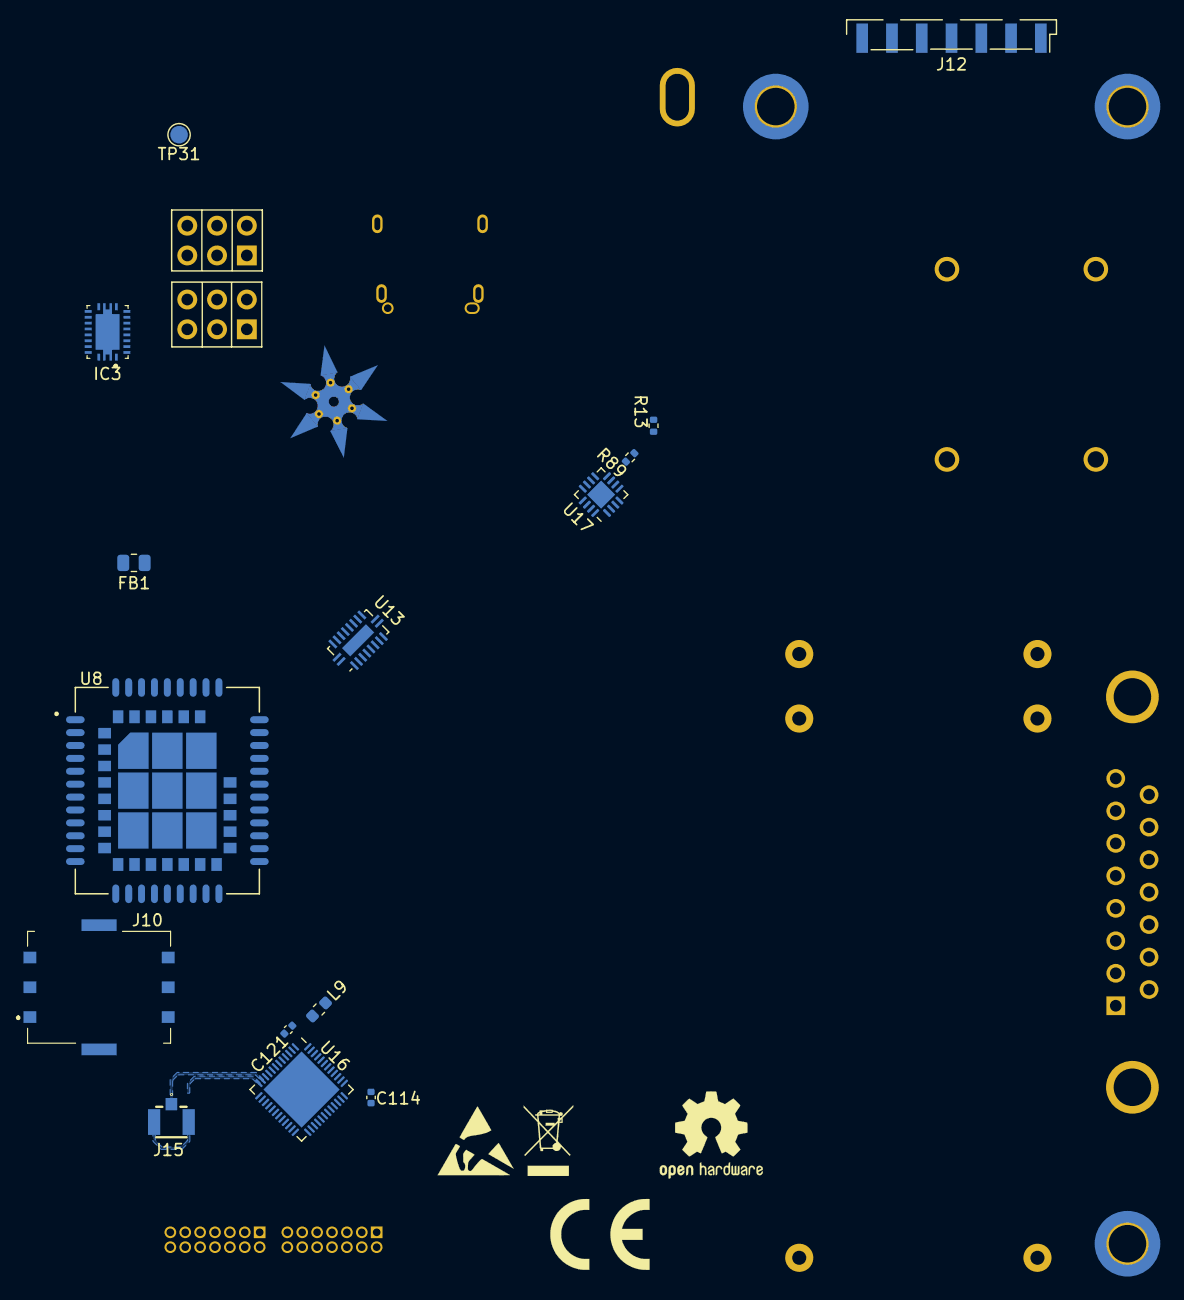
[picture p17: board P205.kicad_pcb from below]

Board: 4 copper layers, 50 parts (15 on the bottom side), 46 nets, no tracks yet.

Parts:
C61, C114: 12p; C_0402_1005Metric
C102, C129: 1u; C_0402_1005Metric
C121: 100n; C_0402_1005Metric
D32: APHBM2012LVBDZGKC; LED_2C
FB1, FB2: BLM21SP601SH1D; R_0805_2012Metric
H3: MH3; MountingHole_3.2mm_M3_DIN965_Pad_TopBottom
H5, H6: MH4; MountingHole_3.2mm_M3_DIN965_Pad_TopBottom
IC3: BQ51050BRHLR
J2: Batt; M404010446
J4: ECG Connector; DSUB-15_Female_Horizontal_P2.77x2.84mm_EdgePinOffset7.70mm_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
J5: AudioJack2_Dual_Switch; NMJ4HHD2
J6, J7: PROG; PinSocket_1x05_P2.54mm_Vertical_SMD_Pin1Right
J8: EXP1; PinSocket_2x07_P1.27mm_Horizontal
J10: SIM_Card; SIM8051601401A
J11, J17: USB/BATT; PinHeader_2x03_P2.54mm_Vertical
J12: Button; ConnButton
J14: 12401598E4#2A; AMPHENOL_12401598E4#2A
J15: U.FL-R-SMT-1(10); CONUFL001-SMD
J16: EXP2; PinSocket_2x07_P1.27mm_Horizontal
L9: 10u; L_0603_1608Metric
NT1: STARGROUND; NINJA_STAR_GROUND_CUT
R13, R93: 5.1k; R_0402_1005Metric
R14, R15, R18: 100k; R_Axial_DIN0516_L15.5mm_D5.0mm_P20.32mm_Horizontal
R54: 0; R_0402_1005Metric
R68: 330; R_0402_1005Metric
R80: 10k; R_0402_1005Metric
R85, R92: 71.5k; R_0402_1005Metric
R89: NC; R_0402_1005Metric
TP26: MOSI; TestPoint_Pad_D1.5mm
TP27: CLK; TestPoint_Pad_D1.5mm
TP28: MISO; TestPoint_Pad_D1.5mm
TP29, TP30: VCAP1; TestPoint_Pad_D1.5mm
TP31: KEYCHAIN; TestPoint_Pad_D1.5mm
U8: SIM7080G; XCVR_SIM7080G
U9: OLED_2.49; PinHeader_1x07_P2.54mm_Vertical_SMD_Pin1Right
U10: LNA; BGU7007115
U13: NXB0108; WQFN-20-1EP_2.5x4.5mm_P0.5mm_EP1x2.9mm
U16: nRF52832; QFN-48-1EP_6x6mm_P0.4mm_EP4.6x4.6mm
U17: PI5C3257; QFN-16-1EP_3x3mm_P0.5mm_EP1.7x1.7mm

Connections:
/AVCC: FB2.1, R54.1, R85.2, R92.2, R93.1
/BATT: FB1.1, J11.3, J11.4, J16.1, J16.2, J17.3, J17.4
/BATT_RAW: C102.1, IC3.4, J2.1, J11.5, J11.6, J17.5, J17.6
/DVCC: D32.1, J6.5, J7.5, J8.1, J8.2, J8.3, J8.5, J16.3, J16.4, J16.5, R89.1, U10.4, U13.19, U16.13, U16.36, U16.48, U17.16
/RST: J6.4, U16.24
/SIMCOM/SIMCARD_CLK: J10.3, U8.16
/SIMCOM/SIMCARD_DATA: J10.7, U8.15
/SIMCOM/SIMCARD_RST: J10.2, U8.17
/SIMCOM/SIMCARD_VDD: J10.1, U8.18
/SIMCOM/SIMCOM_CTS: U8.4, U13.5
/SIMCOM/SIMCOM_RTS: U8.3, U13.6
/SIMCOM/SIMCOM_RX: U8.1, U13.7
/SIMCOM/SIMCOM_TX: U8.2, U13.8
/SIMCOM/SIMCOM_VDD: FB1.2, U8.34, U8.35
/SIMCOM/VDD_EXT: U8.40, U13.2
/V1: J4.12, R14.2
/V2: J4.1, R15.2
/V5: J4.4, R18.2
/V_BUS: C129.1, D32.4, IC3.9, J11.1, J11.2, J14.A4, J14.A9, J14.B4, J14.B9, J17.1, J17.2
/uC1_AIN1_P0.03: J8.7, U16.5
/uC1_AIN2_P0.04: J8.10, U16.6
/uC1_AIN3_P0.05: J8.8, U16.7
/uC1_AIN4_P0.28: J16.8, U16.40
/uC1_AIN5_P0.29: J16.6, U16.41
/uC1_ECG_MISO: TP28.1, U16.16
/uC1_ECG_MOSI: TP26.1, U16.18
/uC1_ECG_SCLK: TP27.1, U16.17
/uC1_NRF52832/NFC1_ANT: J15.1, U16.11
/uC1_NRF52832/NFC2_ANT: J15.2, J15.3, U16.12
/uC1_NRF52832/SWDCLK: J6.3, U16.25
/uC1_NRF52832/SWDIO: J6.2, U16.26
/uC1_NRF52832/XC-: C114.2, U16.35
/uC1_P0.19: J8.4, U16.22
/uC1_P0.20: J8.6, U16.23
/uC1_P0.22: J16.9, U16.27
/uC1_P0.23: J16.7, U16.28
/uC2_uSD_CS: U17.1, U17.2
GNDD: C114.1, C121.2, J6.1, J7.1, J8.11, J8.12, J8.13, J8.14, J10.5, J16.10, J16.11, J16.12, J16.13, J16.14, NT1.2, U8.8, U8.13, U8.19, U8.21, U8.27, U8.30, U8.31, U8.33, U8.36, U8.37, U8.45, U8.63, U8.66, U8.67, U8.69, U8.70, U8.71, U8.72, U8.73, U8.74, U8.75, U8.76, U8.77, U10.1, U10.2, U13.1, U13.3, U13.4, U13.11, U13.17, U13.18, U13.20, U16.31, U16.45, U16.49, U17.3, U17.6, U17.8, U17.10, U17.13
GNDREF: C102.2, C129.2, IC3.1, IC3.11, IC3.20, IC3.21, J2.3, J2.4, J14.A1, J14.A12, J14.B1, J14.B12, J14.S1, NT1.3, R80.2
GNDS: J4.0, NT1.1
unnamed: C121.1, U16.1
unnamed: U8.39, U13.9
unnamed: R13.2, R89.2, U17.7
unnamed: J14.A6, J14.A7, J14.B6, J14.B7
unnamed: L9.2, U16.47
unnamed: R85.1, R92.1
